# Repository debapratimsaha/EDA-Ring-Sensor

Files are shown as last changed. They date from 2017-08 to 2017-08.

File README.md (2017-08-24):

# EDA Sensor Board 
This repository is an initial prototype of a low-cost [Electrodermal Activity](https://en.wikipedia.org/wiki/Electrodermal_activity) Sensor that I was working on in early 2014. This sensor measures electrodermal activity at the index and middle fingers and this current prototype is in a ring form-factor. 

### Circuit Description
The circuit is a resistor divider connected to a Texas Instruments INA337 instrument amplifier. The output is passed through an anti-aliasing filter before being read by the 10-bit ADC in an atTiny85 micro. 

### Firmware Description
The firmware is modelled as a state-machine which reads the ADC values, maps the average of 1s of data bytes into some coloring ranges and then controls an RGB-LED in real-time. The implemented state-machine is:

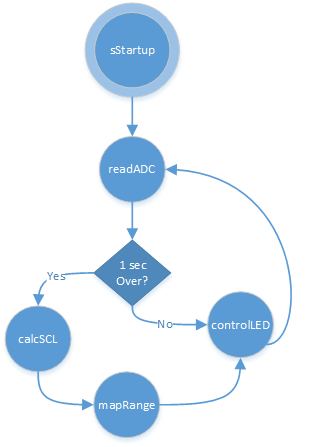
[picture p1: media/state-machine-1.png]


The video below shows the LED going through different phases of operation while the human is going through Forced Maximal Inhalation:

<a href="http://www.youtube.com/watch?feature=player_embedded&v=uJLOnX5DqEU" target="_blank">IMAGE ALT TEXT HERE</a>

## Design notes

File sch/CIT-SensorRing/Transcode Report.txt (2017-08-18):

   ---- Transcoding 'G:\Dropbox\RESEARCH\Knapp Research Group\Projects\CIT Sensor Ring\sch\CIT-SensorRing\sensorring_withflex_v2.GBS' ----   Mon Mar 17 16:23:35 2014

D10   --> D100
D11   --> D101
D12   --> D102
-----------------------------------------------------------------

   ---- Transcoding 'G:\Dropbox\RESEARCH\Knapp Research Group\Projects\CIT Sensor Ring\sch\CIT-SensorRing\sensorring_withflex_v2.GTL' ----   Mon Mar 17 16:23:35 2014

D10   --> D103
D11   --> D104
D12   --> D105
D13   --> D106
D14   --> D107
-----------------------------------------------------------------

   ---- Transcoding 'G:\Dropbox\RESEARCH\Knapp Research Group\Projects\CIT Sensor Ring\sch\CIT-SensorRing\sensorring_withflex_v2.GTO' ----   Mon Mar 17 16:23:35 2014

D10   --> D108
D11   --> D109
D12   --> D110
D13   --> D111
D14   --> D112
-----------------------------------------------------------------

   ---- Transcoding 'G:\Dropbox\RESEARCH\Knapp Research Group\Projects\CIT Sensor Ring\sch\CIT-SensorRing\sensorring_withflex_v2.GTP' ----   Mon Mar 17 16:23:35 2014

D10   --> D113
D11   --> D114
D12   --> D115
D13   --> D116
D14   --> D117
D15   --> D118
D16   --> D119
D17   --> D120
D18   --> D121
D19   --> D122
D20   --> D123
D21   --> D124
D22   --> D125
D23   --> D126
D24   --> D127
-----------------------------------------------------------------

   ---- Transcoding 'G:\Dropbox\RESEARCH\Knapp Research Group\Projects\CIT Sensor Ring\sch\CIT-SensorRing\sensorring_withflex_v2.GBS' ----   Mon Mar 17 16:30:29 2014

D10   --> D100
D11   --> D101
D12   --> D102
-----------------------------------------------------------------

   ---- Transcoding 'G:\Dropbox\RESEARCH\Knapp Research Group\Projects\CIT Sensor Ring\sch\CIT-SensorRing\sensorring_withflex_v2.GTL' ----   Mon Mar 17 16:30:29 2014

D10   --> D103
D11   --> D104
D12   --> D105
D13   --> D106
D14   --> D107
-----------------------------------------------------------------

   ---- Transcoding 'G:\Dropbox\RESEARCH\Knapp Research Group\Projects\CIT Sensor Ring\sch\CIT-SensorRing\sensorring_withflex_v2.GTO' ----   Mon Mar 17 16:30:29 2014

D10   --> D108
D11   --> D109
D12   --> D110
D13   --> D111
D14   --> D112
-----------------------------------------------------------------

   ---- Transcoding 'G:\Dropbox\RESEARCH\Knapp Research Group\Projects\CIT Sensor Ring\sch\CIT-SensorRing\sensorring_withflex_v2.GTS' ----   Mon Mar 17 16:30:29 2014

D10   --> D113
D11   --> D114
D12   --> D115
D13   --> D116
D14   --> D117
D15   --> D118
D16   --> D119
D17   --> D120
D18   --> D121
D19   --> D122
D20   --> D123
D21   --> D124
D22   --> D125
D23   --> D126
D24   --> D127
-----------------------------------------------------------------

   ---- Transcoding 'G:\Dropbox\RESEARCH\Knapp Research Group\Projects\CIT Sensor Ring\sch\CIT-SensorRing\sensorring_withflex_v2.GBS' ----   Mon Mar 17 16:59:33 2014

D10   --> D128
D11   --> D129
D12   --> D130
-----------------------------------------------------------------

   ---- Transcoding 'G:\Dropbox\RESEARCH\Knapp Research Group\Projects\CIT Sensor Ring\sch\CIT-SensorRing\sensorring_withflex_v2.GTL' ----   Mon Mar 17 16:59:33 2014

D10   --> D131
D11   --> D132
D12   --> D133
D13   --> D134
D14   --> D135
-----------------------------------------------------------------

   ---- Transcoding 'G:\Dropbox\RESEARCH\Knapp Research Group\Projects\CIT Sensor Ring\sch\CIT-SensorRing\sensorring_withflex_v2.GTO' ----   Mon Mar 17 16:59:33 2014

D10   --> D136
D11   --> D137
D12   --> D138
D13   --> D139
D14   --> D140
D15   --> D141
D16   --> D142
D17   --> D143
-----------------------------------------------------------------

   ---- Transcoding 'G:\Dropbox\RESEARCH\Knapp Research Group\Projects\CIT Sensor Ring\sch\CIT-SensorRing\sensorring_withflex_v2.GTS' ----   Mon Mar 17 16:59:33 2014

D10   --> D144
D11   --> D145
D12   --> D146
D13   --> D147
D14   --> D148
D15   --> D149
D16   --> D150
D17   --> D151
D18   --> D152
D19   --> D153
D20   --> D154
D21   --> D155
D22   --> D156
D23   --> D157
D24   --> D158
-----------------------------------------------------------------

   ---- Transcoding 'G:\Dropbox\RESEARCH\Knapp Research Group\Projects\CIT Sensor Ring\sch\CIT-SensorRing\sensorring_withflex_v2.GBS' ----   Mon Mar 17 17:21:11 2014

D10   --> D100
D11   --> D101
D12   --> D102
-----------------------------------------------------------------

   ---- Transcoding 'G:\Dropbox\RESEARCH\Knapp Research Group\Projects\CIT Sensor Ring\sch\CIT-SensorRing\sensorring_withflex_v2.GTL' ----   Mon Mar 17 17:21:11 2014

D10   --> D103
D11   --> D104
D12   --> D105
D13   --> D106
D14   --> D107
-----------------------------------------------------------------

   ---- Transcoding 'G:\Dropbox\RESEARCH\Knapp Research Group\Projects\CIT Sensor Ring\sch\CIT-SensorRing\sensorring_withflex_v2.GTO' ----   Mon Mar 17 17:21:11 2014

D10   --> D108
D11   --> D109
D12   --> D110
D13   --> D111
D14   --> D112
D15   --> D113
D16   --> D114
D17   --> D115
-----------------------------------------------------------------

   ---- Transcoding 'G:\Dropbox\RESEARCH\Knapp Research Group\Projects\CIT Sensor Ring\sch\CIT-SensorRing\sensorring_withflex_v2.GTS' ----   Mon Mar 17 17:21:11 2014

D10   --> D116
D11   --> D117
D12   --> D118
D13   --> D119
D14   --> D120
D15   --> D121
D16   --> D122
D17   --> D123
D18   --> D124
D19   --> D125
D20   --> D126
D21   --> D127
D22   --> D128
D23   --> D129
D24   --> D130
-----------------------------------------------------------------

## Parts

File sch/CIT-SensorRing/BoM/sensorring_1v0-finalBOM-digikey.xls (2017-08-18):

Digi-Key Part Number | Manufacturer | Manufacturer Part Number | Customer Reference | Quantity 1 | Description
BAT-HLD-001-ND | LINX TECHNOLOGIES INC | BAT-HLD-001 | BATT | 1 | HOLDER BATTERY 20MM COIN
445-1415-1-ND | TDK CORPORATION (VA) | C1005X5R0J105M050BB | C1, C2 | 2 | CAP CER 1UF 6.3V 20% X5R 0402
490-6246-1-ND | MURATA ELECTRONICS (VA) | GRM1555C1H511GA01D | C3 | 1 | CAP CER 510PF 50V 2% NP0 0402
445-5942-1-ND | TDK CORPORATION (VA) | C1005X5R1H104K050BB | C4, C5, C6, C7 | 4 | CAP CER 0.1UF 50V 10% X5R 0402
490-5437-1-ND | MURATA ELECTRONICS (VA) | BLM15AX100SN1D | FB1 | 1 | FERRITE CHIP 10 OHM 0402
RMCF0402FT40K2CT-ND | STACKPOLE ELECTRONICS INC (VA) | RMCF0402FT40K2 | R1 | 1 | RES 40.2K OHM 1/16W 1% 0402
311-200KLRCT-ND | YAGEO (VA) | RC0402FR-07200KL | R2 | 1 | RES 200K OHM 1/16W 1% 0402 SMD
RMCF0402FT100RCT-ND | STACKPOLE ELECTRONICS INC (VA) | RMCF0402FT100R | R3, R6, R7, R8 | 4 | RES 100 OHM 1/16W 1% 0402
311-1.00MLRCT-ND | YAGEO (VA) | RC0402FR-071ML | R4, R5 | 2 | RES 1.00M OHM 1/16W 1% 0402 SMD
ATTINY85-20MURCT-ND | ATMEL (VA) | ATTINY85-20MUR | U1 | 1 | IC MCU 8BIT 8KB FLASH 20QFN
296-25215-1-ND | TEXAS INSTRUMENTS (VA) | TLV70033DSET | U2 | 1 | IC REG LDO 3.3V 0.2A 6WSON
296-13453-1-ND | TEXAS INSTRUMENTS (VA) | INA337AIDGKT | U3 | 1 | IC OPAMP INSTR 1KHZ 8VSSOP
846-1097-1-ND | ROHM SEMICONDUCTOR(VA) | SMLP36RGB2W3 | U4 | 1 | LED PICOLED RGB 5MA 1510
609-4052-1-ND | FCI (VA) | 10104110-0001LF | X3 | 1 | CONN RCPT STD MICRO USB TYPE B

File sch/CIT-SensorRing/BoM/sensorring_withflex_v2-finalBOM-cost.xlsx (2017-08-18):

Order list for G:/Dropbox/RESEARCH/Knapp Research Group/Projects/CIT Sensor Ring/sch/CIT-SensorRing/sensorring_withflex_v2.sch
Exported from EAGLE with DesignLink
Quantity | Value | Package | RefDes | Manufacturer | Cost ($) | Manuf. Code | DigiKey Part Number | Description
1 | Coin Cell Retainer | CR2032-SMD | BATT | KeyStone | 0.546 | 3082 * | 3082K-ND | Coin Cell Retainer DigiKey - 3082K-ND
2 | 1uF | C1005 | C1, C2 | TDK | 0.1 | C1005X5R0J105M050BB |  | TDK - C1005X5R0J105M050BB - CAPACITOR CERAMIC, 1UF, 6.3V, X5R, 20%, 0402
1 | 0.5nF | C0402 | C3 | AVX | 0.0525 | 04025C501JAT2A | 04025C501JAT2A-ND | AVX-CAP CER, 500pF, 5%, 50V, X7R, DigiKey - 04025C501JAT2A-ND
4 | 0.1uF | C0402 | C4, C5, C6, C7 | TDK | 0.13 | C1005X5R1H104K050BB |  | TDK - C1005X5R1H104K050BB - CAP CERAMIC, 0.1UF, 50V, X5R, 0402
1 | 10 Ohm @ 100MHz | FB0402 | FB1 | MURATA | 0.11 | BLM15AX100SN1D | 490-5437-1-ND | MURATA - 10 Ohm @ 100MHz, 1.74A, 20mOhm max, 0402
1 | 40k | R0402 | R1 | VISHAY/DALE | 0.083 | CRCW040240K2FKED |  | VISHAY DALE - CRCW040240K2FKED - RESISTOR, THICK FILM, 40.2KOHM, 63mW, 1%
1 | 200k | R0402 | R2 | VISHAY/DALE | 0.083 | CRCW0402200KFKED |  | VISHAY DALE - CRCW0402200KFKED - RESISTOR, THICK FILM, 200KOHM, 63mW, 1%
4 | 0.1k | R0402 | R3, R6, R7, R8 | VISHAY SFERNICE | 0.1 | CH0402-100RGF * (311-100LRCT-ND) |  | VISHAY SFERNICE - CH0402-100RGF - RESISTORS, 0402, 100R
2 | 1M | R0402 | R4, R5 | VISHAY/DALE | 0.176 | CRCW04021M00FKED |  | VISHAY DALE - CRCW04021M00FKED - RESISTOR, THICK FILM, 1MOHM, 63mW, 1%
1 | ATTiny85 | 20M1 | U1 | ATMEL | 1.8 | ATTINY85-20MUR | ATTINY85-20MURCT-ND 20-QFN | DigiKey ATTINY85-20MURCT-ND 20-QFN
1 | TLV70033 | DSE6 | U2 | TI | 0.59 | TLV70033DSET | 296-25215-1-ND | TEXAS INSTRUMENTS - TLV70033DSET - LDO DigiKey - 296-25215-1-ND
1 | INA337 | DGK8 | U3 | TI | 5.44 | INA337AIDGKT | 296-13453-1-ND | TEXAS INSTRUMENTS - INA337 - InAmp DigiKey - 296-13453-1-ND
1 | RGB PICOLED | PICOLED-1MM_1MM5 | U4 | RohmSemi | 1.15 | SMLP36RGB2W3 | 846-1097-1-ND | Rohm Semi - RGB PicoLED 5mA Digikey - 846-1097-1-ND
1 | USB Recep | USB-MICROB | X3 | FCI | 0.46 | 10118192-0001LF | 609-4613-1-ND | FCI CONN USB MICRO B RECPT SMT R/A Digikey 609-4613-1-ND
 |  |  |  |  | 10.8205

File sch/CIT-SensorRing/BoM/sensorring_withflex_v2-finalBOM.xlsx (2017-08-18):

Order list for G:/Dropbox/RESEARCH/Knapp Research Group/Projects/CIT Sensor Ring/sch/CIT-SensorRing/sensorring_withflex_v2.sch
Exported from EAGLE with DesignLink
Quantity | Value | Package | RefDes | Manufacturer | Manuf. Code | DigiKey Part Number | Description
1 | Coin Cell Retainer | CR2032-SMD | BATT | KeyStone | 3082 | 3082K-ND | Coin Cell Retainer DigiKey - 3082K-ND
2 | 1uF | C1005 | C1, C2 | TDK | C1005X5R0J105M050BB |  | TDK - C1005X5R0J105M050BB - CAPACITOR CERAMIC, 1UF, 6.3V, X5R, 20%, 0402
1 | 0.5nF | C0402 | C3 | AVX | 04025C501JAT2A | 04025C501JAT2A-ND | AVX-CAP CER, 500pF, 5%, 50V, X7R, DigiKey - 04025C501JAT2A-ND
4 | 0.1uF | C0402 | C4, C5, C6, C7 | TDK | C1005X5R1H104K050BB |  | TDK - C1005X5R1H104K050BB - CAP CERAMIC, 0.1UF, 50V, X5R, 0402
1 | 10 Ohm @ 100MHz | FB0402 | FB1 | MURATA | BLM15AX100SN1D | 490-5437-1-ND | MURATA - 10 Ohm @ 100MHz, 1.74A, 20mOhm max, 0402
1 | 40k | R0402 | R1 | VISHAY/DALE | CRCW040240K2FKED |  | VISHAY DALE - CRCW040240K2FKED - RESISTOR, THICK FILM, 40.2KOHM, 63mW, 1%
1 | 200k | R0402 | R2 | VISHAY/DALE | CRCW0402200KFKED |  | VISHAY DALE - CRCW0402200KFKED - RESISTOR, THICK FILM, 200KOHM, 63mW, 1%
4 | 0.1k | R0402 | R3, R6, R7, R8 | VISHAY SFERNICE | CH0402-100RGF |  | VISHAY SFERNICE - CH0402-100RGF - RESISTORS, 0402, 100R
2 | 1M | R0402 | R4, R5 | VISHAY/DALE | CRCW04021M00FKED |  | VISHAY DALE - CRCW04021M00FKED - RESISTOR, THICK FILM, 1MOHM, 63mW, 1%
1 | ATTiny85 | 20M1 | U1 | ATMEL | ATTINY85-20MUR | ATTINY85-20MURCT-ND 20-QFN | DigiKey ATTINY85-20MURCT-ND 20-QFN
1 | TLV70033 | DSE6 | U2 | TI | TLV70033DSET | 296-25215-1-ND | TEXAS INSTRUMENTS - TLV70033DSET - LDO DigiKey - 296-25215-1-ND
1 | INA337 | DGK8 | U3 | TI | INA337AIDGKT | 296-13453-1-ND | TEXAS INSTRUMENTS - INA337 - InAmp DigiKey - 296-13453-1-ND
1 | RGB PICOLED | PICOLED-1MM_1MM5 | U4 | RohmSemi | SMLP36RGB2W3 | 846-1097-1-ND | Rohm Semi - RGB PicoLED 5mA Digikey - 846-1097-1-ND
1 | USB Recep | USB-MICROB | X3 | FCI | 10118192-0001LF | 609-4613-1-ND | FCI CONN USB MICRO B RECPT SMT R/A Digikey 609-4613-1-ND

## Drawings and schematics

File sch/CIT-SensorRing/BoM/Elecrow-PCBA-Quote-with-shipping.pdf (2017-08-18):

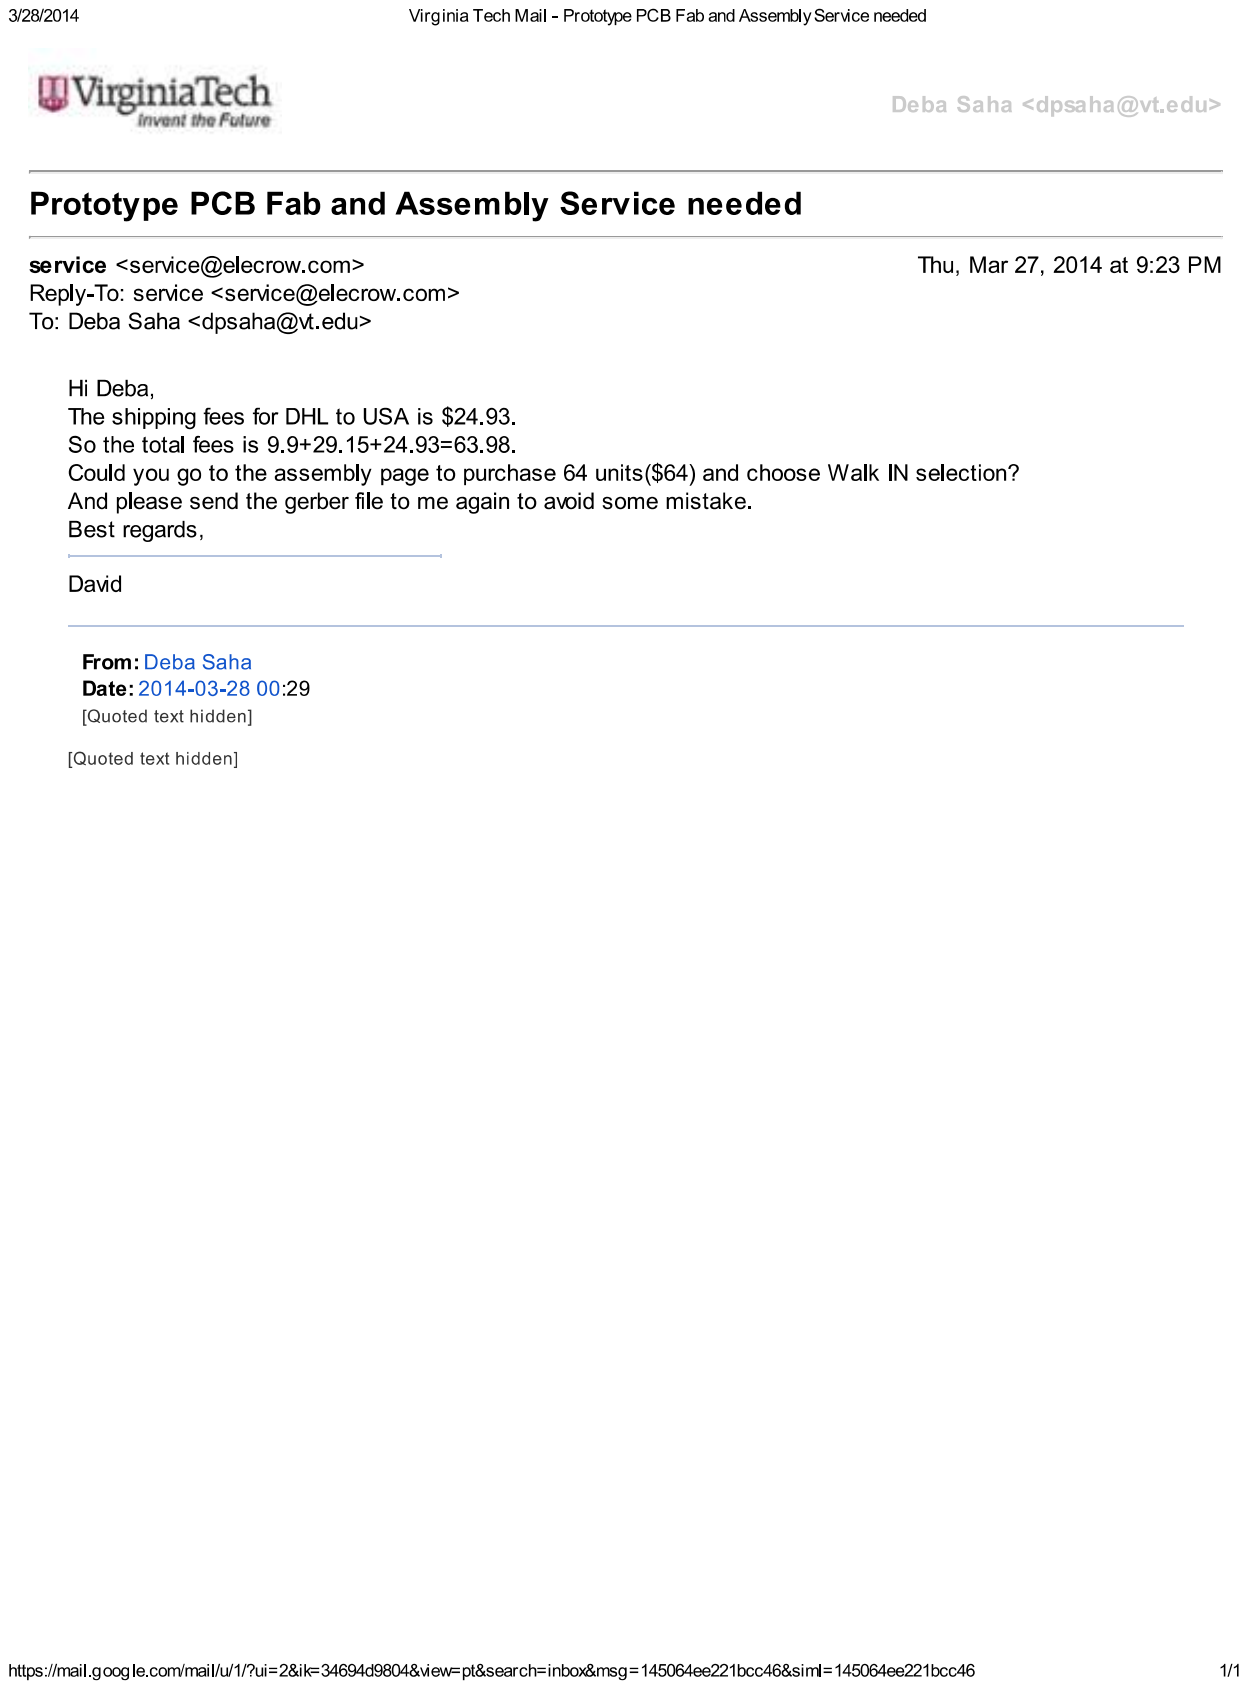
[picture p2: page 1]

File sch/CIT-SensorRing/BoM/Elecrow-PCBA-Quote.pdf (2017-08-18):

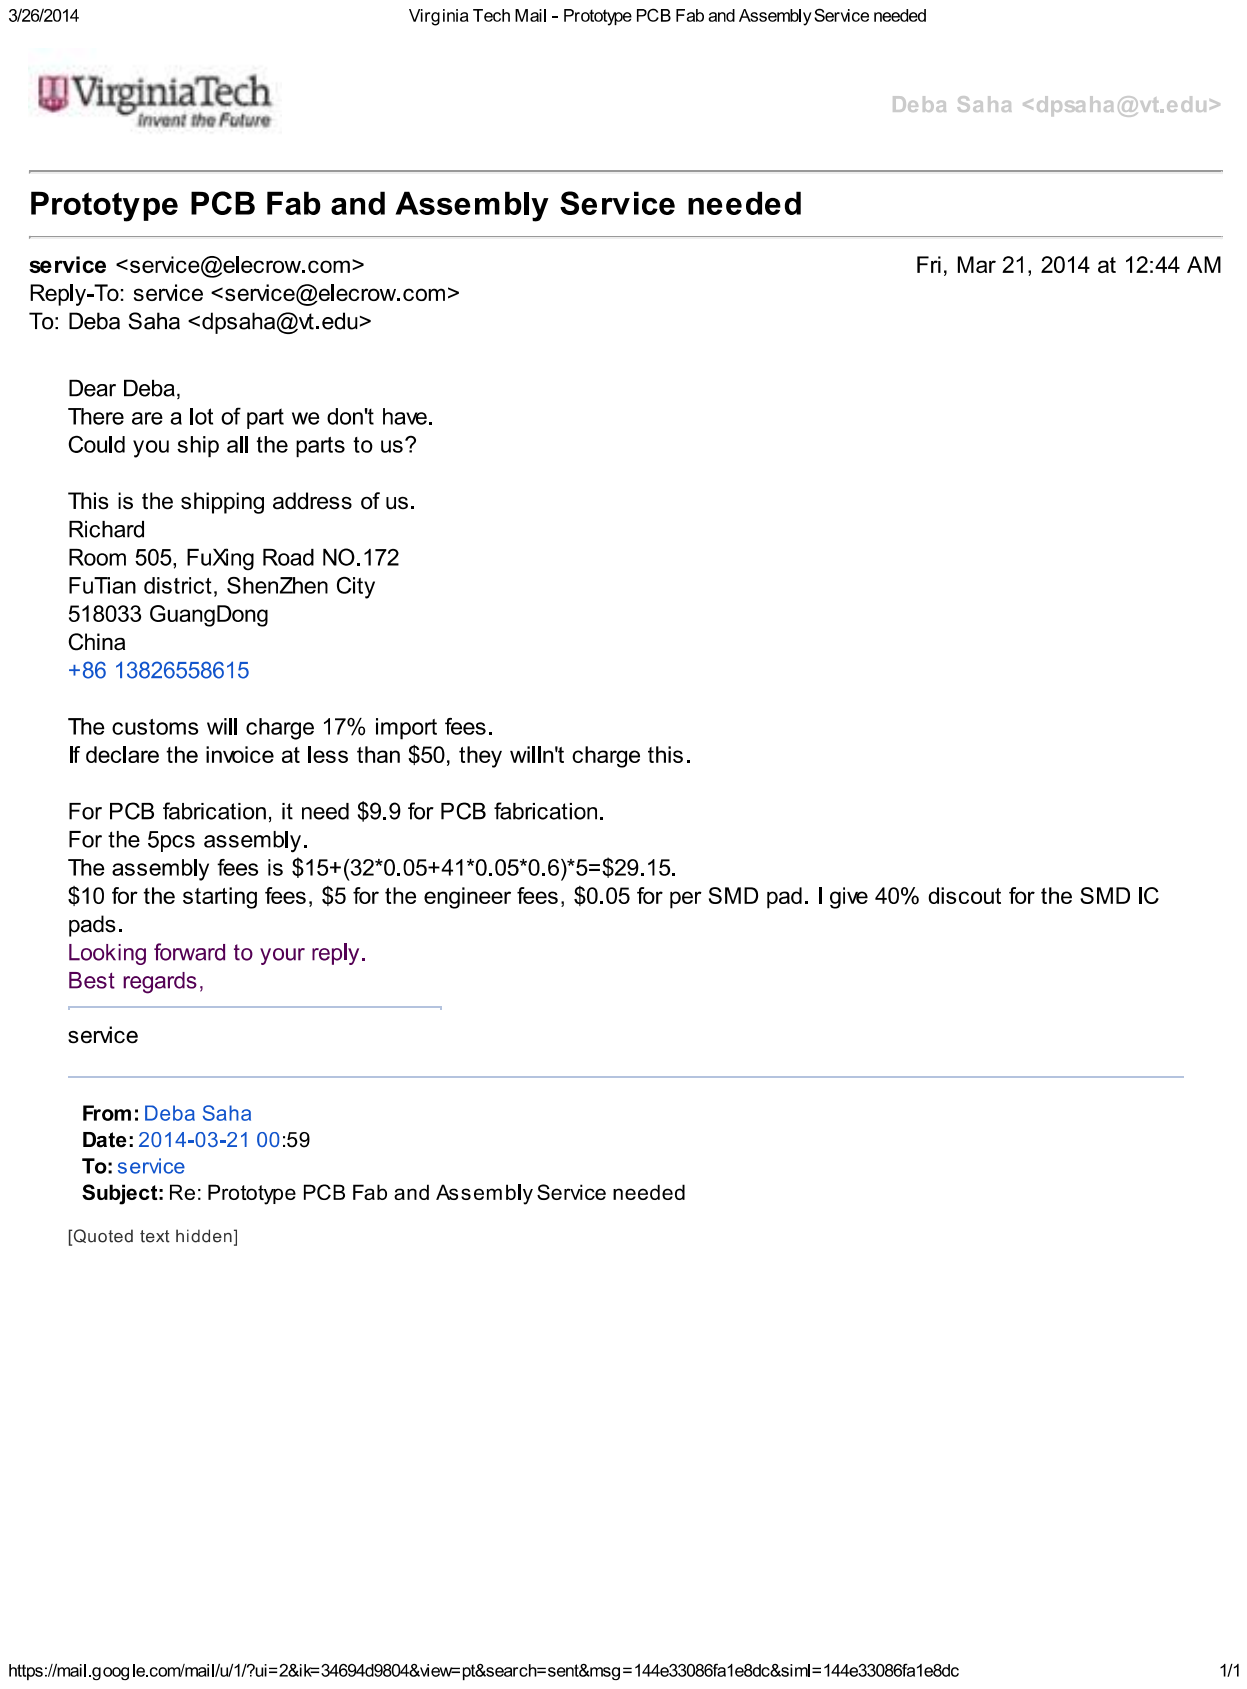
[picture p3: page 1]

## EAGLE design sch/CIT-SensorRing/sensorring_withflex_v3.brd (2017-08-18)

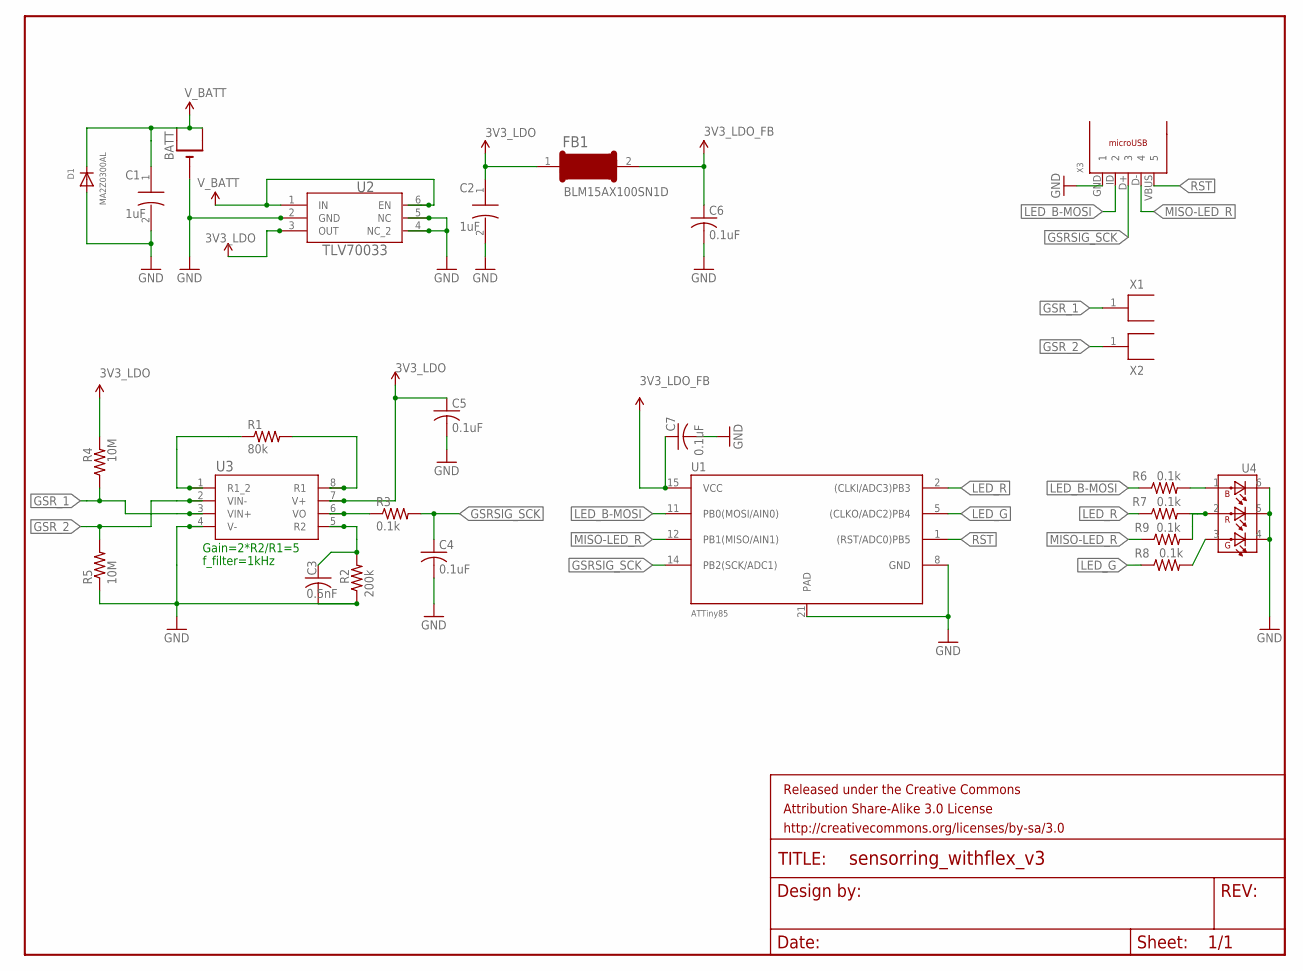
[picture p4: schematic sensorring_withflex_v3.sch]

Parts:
BATT: CR2032SMT; CR2032-SMD
C1, C2: 1uF; C1005; MPN C1005X5R0J105M050BB
C3: 0.5nF; C0402
C4, C5, C6, C7: 0.1uF; C0402; MPN C1005X5R1H104K050BB
D1: MA2Z0300AL; SOD-323F
FB1: BLM15AX100SN1D; 0402
FRAME1: FRAME-LETTER; CREATIVE_COMMONS
R1: 80k; R0402; MPN CRCW040240K2FKED
R2: 200k; R0402; MPN CRCW0402200KFKED
R3, R6, R7, R8: 0.1k; R0402; MPN CH0402-100RGF
R4, R5: 10M; R0402; MPN CRCW04021M00FKED
R9: 0.1k; R0402
U1: ATTiny85; 20M1; MPN ATTINY84-15MZ
U2: TLV70033; DSE6; MPN TLV70033DSET
U3: INA337_DGK_8; DGK8
U4: PICOLED-RGB-1MMX1MM5; PICOLED-1MM_1MM5
X1, X2: GSR_FLEX; GSR_FLEX_LEAD
X3: USB-MICRO-B; USB-MICROB

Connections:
3V3_LDO: C2.1, C5.1, FB1.1, R4.2, U2.3 (OUT), U3.7 (V+)
3V3_LDO_FB: C6.1, C7.1, FB1.2, U1.15 (VCC)
GND: BATT.-, C1.2, C2.2, C3.2, C4.2, C5.2, C6.2, C7.2, D1.A, R2.1, R5.1, U1.8 (GND), U1.21 (PAD), U2.2 (GND), U2.4 (NC_2), U2.5 (NC), U3.4 (V-), U4.4 (A_G), U4.5 (A_R), U4.6 (A_B), X3.GND (1)
GSRSIG_SCK: C4.1, R3.2, U1.14 (PB2(SCK/ADC1)), X3.D+ (3)
GSR_1: R4.1, U3.3 (VIN+), X1.1
GSR_2: R5.2, U3.2 (VIN-), X2.1
LED_B-MOSI: R6.1, U1.11 (PB0(MOSI/AIN0)), X3.ID (2)
LED_G: R8.1, U1.5 ((CLKO/ADC2)PB4)
LED_R: R7.1, U1.2 ((CLKI/ADC3)PB3)
MISO-LED_R: R9.1, U1.12 (PB1(MISO/AIN1)), X3.D- (4)
unnamed: R3.1, U3.6 (VO)
unnamed: R6.2, U4.1 (C_B)
unnamed: R1.2, U3.8 (R1)
unnamed: R1.1, U3.1 (R1_2)
unnamed: R8.2, U4.3 (C_G)
unnamed: C3.1, R2.2, U3.5 (R2)
unnamed: R7.2, R9.2, U4.2 (C_R)
RST: U1.1 ((RST/ADC0)PB5), X3.VBUS (5)
V_BATT: BATT.+$1 (+), BATT.+$2 (+1), C1.1, D1.C, U2.1 (IN), U2.6 (EN)

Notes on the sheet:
Gain=2*R2/R1=5
f_filter=1kHz

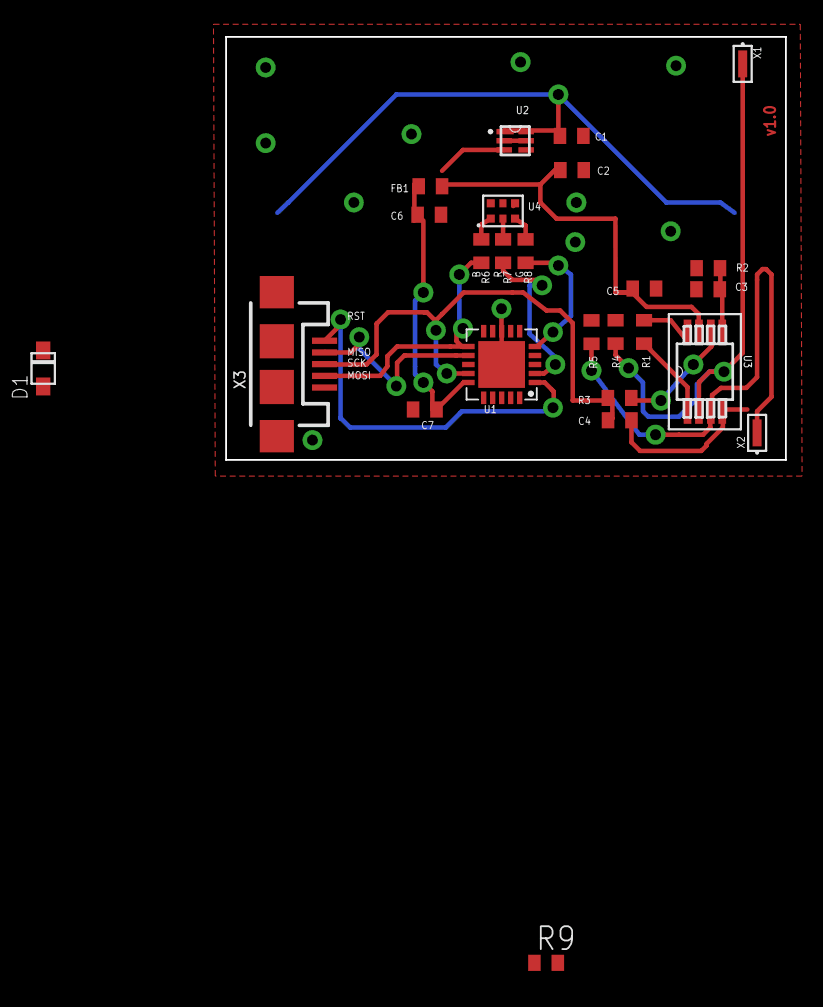
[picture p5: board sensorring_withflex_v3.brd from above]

Board: 2 copper layers, 31.1 x 23.5 mm, 27 parts (1 on the bottom side), 19 nets.

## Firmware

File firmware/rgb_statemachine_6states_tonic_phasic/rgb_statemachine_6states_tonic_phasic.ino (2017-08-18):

/*  CIT Sensor Ring Project
**  Code by : DebaPSaha 
**  Date    : 5/22/14
**  Ver     : 1.0     
*/    

// ---------- Headers -------------------------	//
#include <avr/io.h>                    								// Adds useful constants
#include <util/delay.h>                								// Adds delay_ms and delay_us functions
#include <SoftwareSerial.h>            							        // Library for software serial, ATtiny doesn't have hardware serial
#include "Arduino.h"                   								// Useful constants
	
// ------------- Definitions ------------------	//
#define DEBUG_MODE          	false      							// Serial prints are sent to the prompt
#define F_CPU               	8000000    							// delay.h uses this value, we have set the cpu freq to be 8MHz
#define INITPULSETIME       	30         							// LED Pulse half-period during initialization 
#define MAX_PWIDTH          	20         							// LED PWM max pulse width
#define SIZEOF_DATA_ARRAY   	64        							// Data_Array is the array containing time series
#define SCL_LOOPCOUNTER         4000                                                            // Assuming 250uS for each loop, 4000 sets the SCL polling at 1sec
//#define LEDTRANSITION_LOOPDELAY (int)(500*1000)/(MAX_PWIDTH*21);


#if DEBUG_MODE
// Port Definitions
#define rxPin 3
#define txPin 4
// Instantiate serial port
SoftwareSerial mySerial(rxPin, txPin);
#else
// Define the LED Pins    
#define LED_R    3              // Pin 3 -- Red LED
#define LED_G    4              // Pin 4 -- Green LED
#endif
#define LED_B    0              // Pin 0 -- Blue LED

// Define ADC input 
#define GSR_SIG  1              // Pin 2 -- GSR Signal | 1 = Analog Pin 1


// -------------- Global Vars ------------------------//
int TH[5];                                            // This var stores the region of operation of LED wrt GSR values
int gsrData[SIZEOF_DATA_ARRAY];                       // This array stores the values of GSR data to compute SCL
float tonicSCL;
int loopCount=SCL_LOOPCOUNTER-1, dataCount=0;
enum ledColor {Red,Green,Blue,Null};
enum stateColor {OnlyRed,OnlyGreen,OnlyBlue,Magenta,Yellow,Cyan};
stateColor currentState,toState=OnlyRed;

//------------- Function Prototypes -------------//
void pulse(int, int);
void stateMachine(int);
void attinySWpwm(int,int);
void setupExtraPWM(void);
void stateTransition(stateColor,stateColor);
void maintainState(stateColor);
float calcSCL(void);
void mapLEDrange(float);

// --------------- Start of Program -----------------------//  

/************** Function setup() **********/
void setup() {  
  // Setup pinmodes
#if DEBUG_MODE  
  mySerial.begin(9600);  
#else
  pinMode(LED_R, OUTPUT);     
  pulse (LED_R,2);
  pinMode(LED_G, OUTPUT);     
  pulse (LED_G,2);
#endif  
  pinMode(LED_B, OUTPUT);     
  pulse (LED_B,2);
  
  pinMode(GSR_SIG, INPUT); 

  // Toggle Pin setup
  pinMode(1,OUTPUT)  ;        
  
  // Setup an Extra PWM 
  setupExtraPWM();
}


//******************* LOOP ***********************//
void loop() {
  int gsrVal = analogRead(GSR_SIG);
  gsrData[dataCount++]=gsrVal;
  if (dataCount==SIZEOF_DATA_ARRAY) dataCount=0;
  
  loopCount++;
  if (loopCount==4000){
    tonicSCL =  calcSCL();
    mapLEDrange(tonicSCL);
    loopCount = 0;
  }

#if DEBUG_MODE
  mySerial.println((int)tonicSCL);
  delay(100);
#else
  stateMachine(gsrVal);
#endif
}


/************** Function mapLEDrange() **********/
void mapLEDrange(float tonicSCL){
// Define thresholds and colors
/*<-- Red -->|| TH0 ||<-- Magenta -->|| TH1 ||<-- Yellow -->| ... 
   ... | TH2 ||<-- Cyan -->|| TH3 ||<-- Green -->|| TH4 ||<-- Blue --> -*/

  //------------ Method I --------------//
//  int stepSize = (int)(1023 - tonicSCL)/6;             //This is the step sie for the LED color ranges
//  for (int i=1;i<6;i++)  TH[i-1] = 1023-i*stepSize;    //Map the LED ranges according to the SCL value  
  
  //------------ Method II -------------//
  int upLim,lowLim;
  if (tonicSCL < 300){
    upLim = 300;  lowLim = 0;
  }else if(tonicSCL < 700){
    upLim = 700;  lowLim = 301;  
  }else {
    upLim = 1023;  lowLim = 701;  
  }
  int stepSize = (int)(upLim - lowLim + 100)/6;           //This is the step sie for the LED color ranges
  for (int i=1;i<6;i++)  TH[i-1] = upLim - i*stepSize;    //Map the LED ranges according to the SCL value  
  
}

/************** Function stateMachine() **********/
void stateMachine(int gsrVal){
#if DEBUG_MODE  
  delay(20);                              // Delay needed for the serial to work   
#else  
//  attinySWpwm(LED_R,50);//map(gsrVal,500,1023,0,400));
//  OCR1B = 10;//map(gsrVal,500,1023,0,250);    // Green LED
//  OCR0A = 10;//map(gsrVal,500,1023,0,10);    // Blue LED

  currentState = toState;                  // Store the previous state
  if (gsrVal>=TH[0]){
    toState=OnlyRed;
  }else if(gsrVal<TH[0] && gsrVal>=TH[1]){
    toState=Magenta;
  }else if(gsrVal<TH[1] && gsrVal>=TH[2]){
    toState=Yellow;
  }else if(gsrVal<TH[2] && gsrVal>=TH[3]){
    toState=Cyan;
  }else if(gsrVal<TH[3] && gsrVal>=TH[4]){
    toState=OnlyGreen;
  }else if(gsrVal<TH[4]){
    toState=OnlyBlue;
  }
  
  // Choose whether to transition or maintain state
  if (toState == currentState){
    maintainState(currentState);
  }else{
    stateTransition(currentState,toState);  
  }
#endif  
}

/************** Function maintainState() **********/
void maintainState(stateColor currentState){
    switch (currentState){
    case OnlyRed:
      attinySWpwm(LED_R,MAX_PWIDTH);
      break;
    case OnlyBlue:
      OCR0A = MAX_PWIDTH;
      break;
    case OnlyGreen:
      OCR1B = MAX_PWIDTH;
      break;
    case Magenta:
      attinySWpwm(LED_R,MAX_PWIDTH);
      OCR0A = MAX_PWIDTH;
      break;
    case Yellow:
      OCR1B = MAX_PWIDTH;
      attinySWpwm(LED_R,MAX_PWIDTH);
      break;
    case Cyan:
      OCR0A = MAX_PWIDTH;
      OCR1B = MAX_PWIDTH;
      break;
    }
}

/************** Function stateTransition() **********/
void stateTransition(stateColor currentState, stateColor toState){  
  ledColor toDec1=Null,toDec2=Null,toInc1=Null,toInc2=Null;
  
  if (toState == OnlyRed){
    switch (currentState){
    case Magenta  :  toDec1=Blue;
    case Yellow   :  toDec1=Green; 
    case Cyan     :  toDec1=Blue; toDec2=Green; toInc1=Red;
    case OnlyGreen:  toDec1=Green; toInc1=Red;
    case OnlyBlue :  toDec1=Blue; toInc1=Red;
    }      
  }else if (toState == Magenta){
    switch (currentState){
    case OnlyRed  :  toInc1=Blue;
    case Yellow   :  toDec1=Green; toInc1=Blue;
    case Cyan     :  toDec1=Green; toInc1=Red;
    case OnlyGreen:  toDec1=Green; toInc1=Red; toInc2=Blue; 
    case OnlyBlue :  toInc1=Red;
    }      
  }else if (toState == Yellow){
    switch (currentState){
    case OnlyRed  :  toInc1=Green; 
    case Magenta  :  toDec1=Blue; toInc1=Green; 
    case Cyan     :  toDec1=Blue; toInc1=Red;
    case OnlyGreen:  toInc1=Red;
    case OnlyBlue :  toDec1=Blue; toInc1=Red; toInc2=Green;
    }      
  }else if (toState == Cyan){
    switch (currentState){
    case OnlyRed  :  toDec1=Red; toInc1=Green;toInc2=Blue;
    case Magenta  :  toDec1=Red; toInc1=Green;
    case Yellow   :  toDec1=Red; toInc1=Blue;
    case OnlyGreen:  toInc1=Blue;
    case OnlyBlue :  toInc1=Green;
    }      
  }else if (toState == OnlyGreen){
    switch (currentState){
    case OnlyRed  :  toDec1=Red; toInc1=Green;
    case Magenta  :  toDec1=Blue; toDec2=Red; toInc1=Green;
    case Yellow   :  toDec1=Red; 
    case Cyan     :  toDec1=Blue;
    case OnlyBlue :  toDec1=Blue;toInc1=Green;
    }      
  }else if (toState == OnlyBlue){
    switch (currentState){
    case OnlyRed  :  toDec1=Red; toInc1=Blue;   
    case Magenta  :  toDec1=Red;
    case Yellow   :  toDec1=Green; toDec2=Red; toInc1=Blue;
    case Cyan     :  toDec1=Green;
    case OnlyGreen:  toDec1=Green;toInc1=Blue;
    }      
  }
  
  //loop for LED increasing and decreasing
  for (int i=0,j=MAX_PWIDTH ; i<=MAX_PWIDTH && j>=0 ; i++,j--){
    switch (toInc1){
    case Red    :  attinySWpwm(LED_R,i+1); break;
    case Blue   :  OCR0A = i; break;
    case Green  :  OCR1B = i; break;
    case Null   :  break;
    }
    switch (toInc2){
    case Red    :  attinySWpwm(LED_R,i+1); break;
    case Blue   :  OCR0A = i; break;
    case Green  :  OCR1B = i; break;
    case Null   :  break;
    }
    switch (toDec1){
    case Red    :  attinySWpwm(LED_R,j+1); if(j==0) digitalWrite(LED_R,LOW); break;
    case Blue   :  OCR0A = j; break;
    case Green  :  OCR1B = j; break;
    case Null   :  break;
    }
    switch (toDec2){
    case Red    :  attinySWpwm(LED_R,j+1); if(j==0) digitalWrite(LED_R,LOW); break;
    case Blue   :  OCR0A = j; break;
    case Green  :  OCR1B = j; break;
    case Null   :  break;
    }
    delay(1000);
  }
}


/************** Function calcSCL() *************/
float calcSCL(){
  uint32_t gsrSCLvalue=0;
  for (int i=0;i<SIZEOF_DATA_ARRAY;i++){
    gsrSCLvalue += gsrData[i];
  }
  return gsrSCLvalue/SIZEOF_DATA_ARRAY;
}

/************** Function attinyPWM() **********/
void attinySWpwm(int pin, int pwmValue){
  digitalWrite(pin,HIGH);
  delayMicroseconds(pwmValue);
  digitalWrite(pin,LOW);
  delayMicroseconds(1023-pwmValue);
}

/************** Function pulse() *************/
void pulse(int pin, int times) {
  do {
    digitalWrite(pin, HIGH);
    delay(INITPULSETIME);
    digitalWrite(pin, LOW);
    delay(INITPULSETIME);
  } 
  while (times--);
}
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

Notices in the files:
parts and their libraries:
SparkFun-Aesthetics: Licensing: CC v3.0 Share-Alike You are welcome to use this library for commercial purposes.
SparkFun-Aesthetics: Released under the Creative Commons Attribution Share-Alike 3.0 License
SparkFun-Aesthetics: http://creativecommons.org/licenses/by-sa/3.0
